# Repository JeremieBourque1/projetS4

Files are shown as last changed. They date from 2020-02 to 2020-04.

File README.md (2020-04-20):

# RoboAide



## Description
RoboAide is a project to improve a DIY robotic arm used for mobility assistance. This repository contains code for a GUI application, Arduino code for the control of the arm's motors as well as CAD parts for a 3D printed shell for the arm segments and joints. The application is made in Python using PySide2 and communicates the desired motor positions via USB serial communication with the Arduio/OpenCR board.<br/>
Due to the team's limitation in regards to access to the robotic arm, a smaller prototype version of the arm was built and it was with it that the software was written and tested on. However, the 3D printed shell was designed for the actual arm. In a future version, the software will be adapted for the real arm as well.

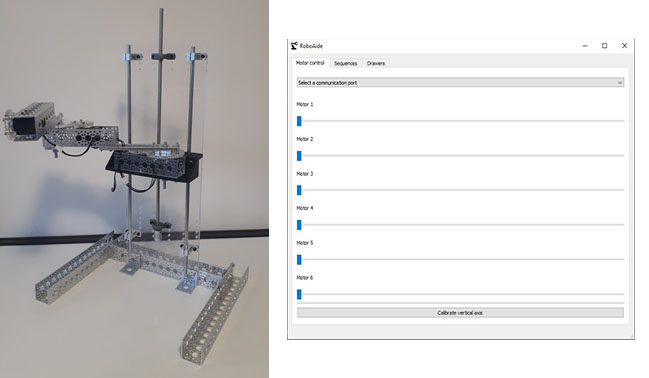
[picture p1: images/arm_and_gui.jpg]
Image of arm prototype and GUI app


## Overview of the application

The application is written in Python and is designed to run on Windows but should also run on other platforms, although this was not tested extensively.
The application contains three tabs: "Motor control", which is for moving the arm's motors individually in joint mode, "Sequences", which is for creating move sequences and executing them, and "Drawers", which is for opening and closing drawers.
It is to be noted that the code controlling the arm is split into two parts.The first is in the main and runs the openCR code for all of the arm's movements. The second is in the Vertical_Axis branch and runs the arduino code which moves the vertical motor.

*NOTE*: follow the instructions section before launching the application.

### Motor control
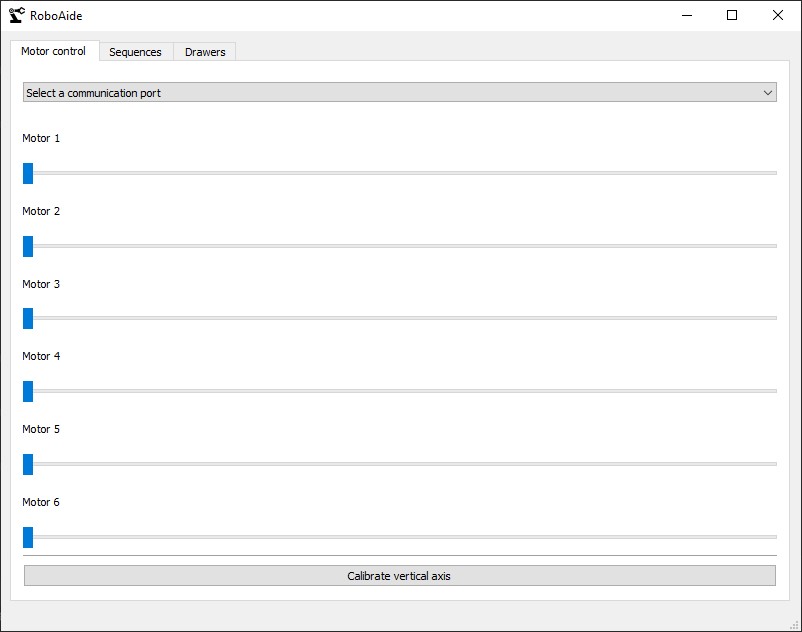
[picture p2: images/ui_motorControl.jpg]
Image of the motor control tab
<br/>
To start the connection, select the appropriate communication port in the drop-down menu. Once connected, moving the sliders will move the motors.

### Sequences
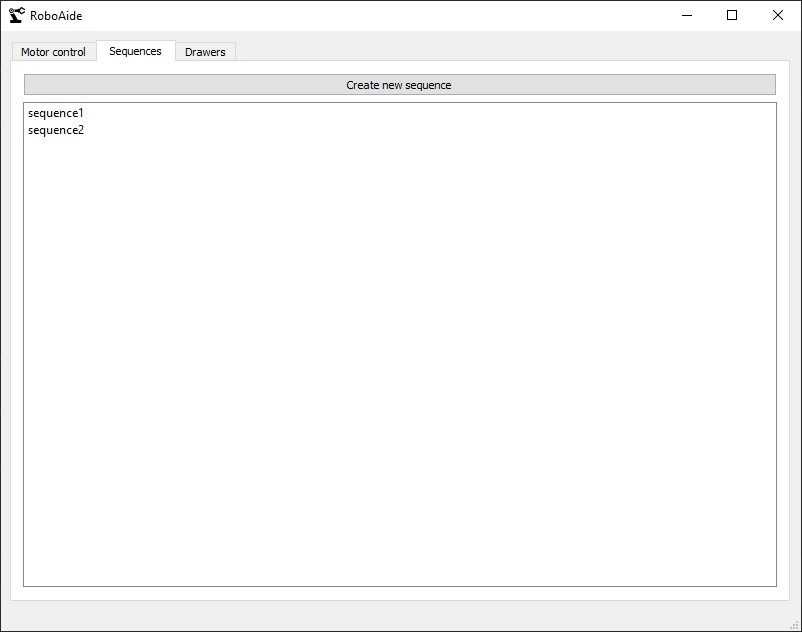
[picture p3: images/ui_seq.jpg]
Image of the sequences tab
<br/>
Here, you can see the list of user-created sequences. To execute a sequence, double click the sequence.<br/><br/>
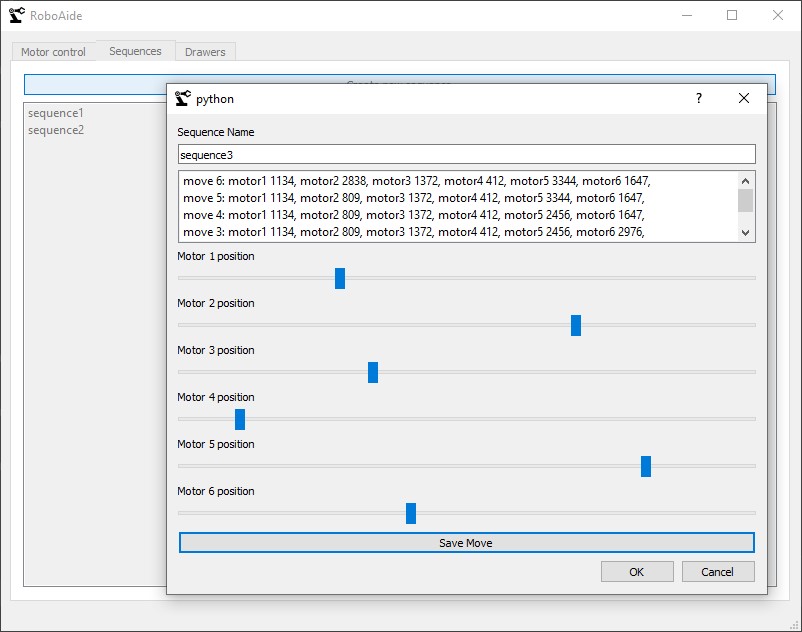
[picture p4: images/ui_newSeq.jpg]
Image of the new sequence window
<br/>
To create a new sequence, click the "Create new sequence" button, which will open this window. You can move the sliders to the desired position, then click "Save move" and create the next move. Double clicking a saved move will move the arm to that position. When done, click "ok".

### Drawers
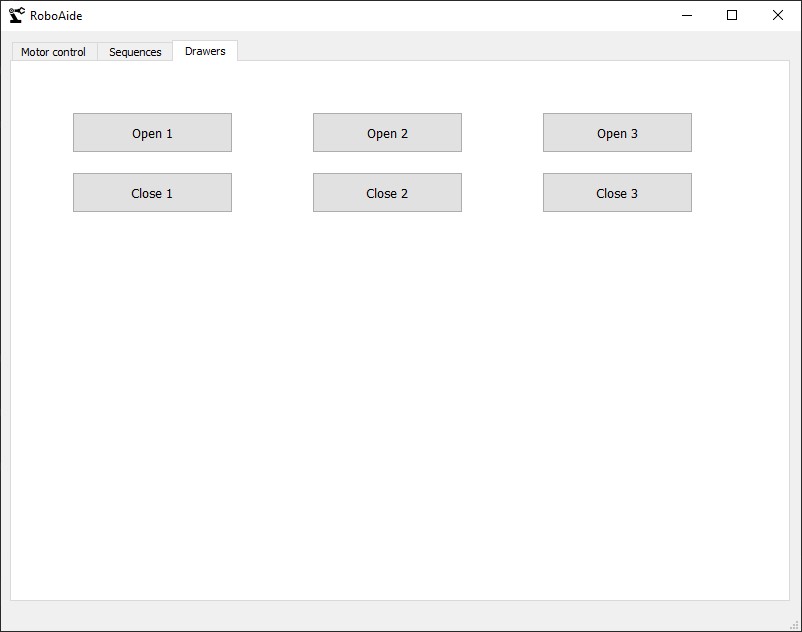
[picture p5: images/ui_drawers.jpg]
Image of the drawers tab
<br/>
This tab makes it possible to open and close the drawers. Note that this feature is not yet implemented in the controller, so the buttons currently do nothing. The feature will be implemented in a future version.

## Hardware Requirements
* 1x PC running Windows (may also run on other platforms, but hasn't been tested)
* 1x OpenCR board
* 3x Dynamixel motors
* 2x Twidec NJK-5002J inductive proximity sensor
* 1x L298N DC motor drive
* 1x Cytron 12v DC motor
* Robot arm prototype (see hardware documentation for more information)

## Software requirements

### UI Dependencies
* Python 3.7 or later (https://www.python.org/downloads/)
* pip (https://www.liquidweb.com/kb/install-pip-windows/)
* PySide2 
* PySerial

The necessary Python libraries can be installed with `pip install -r requirements.txt`

### Controller dependencies
* Arduino IDE (https://www.arduino.cc/en/main/software)
* OpenCR driver (should install automatically when the board is plugged into the PC)
* OpenCR board support for Arduino IDE (http://emanual.robotis.com/docs/en/parts/controller/opencr10/#install-on-windows)

## Instructions for the robot arm
1. Install all dependencies
2. Plug in the OpenCR board to the PC via USB
3. Launch Arduino IDE and choose the right board and communication port.
4. Upload the Arduino code
5. Run RoboAide.py with python to launch the GUI application. To do this, open a command prompt, change the directory to this project's directory and run this command `python UI/RoboAide.py`

## Instruction for the vertical axis
1. Plug all electronic according to the wiring diagram (see below)
2. Once plugged in, run and push the main.ino code which is under the Arduino_code folder to your arduino.
3. Open Pycharm and run the RoboAide.py file which can be found under the ui folder.
4. An application should pop up. Choose your communication port on the application and wait for 10 seconds to let the arduino initialise its comm port.
5. The vertical axis is ready to be calibrated. Press "calibrate vertical axis" button. Once the robot arm has been calibrated, you're free to use the 
slider #4 to move the vertical axis.

## Software documentation
All software documentation can be viewed [here](https://jeremiebourque1.github.io/projetS4/)

## Hardware documentation
### Robotic arm prototype
*The bill of materials for the robot arm prototype can be viewed [here](https://github.com/JeremieBourque1/projetS4/blob/master/BOM_proto.xlsx?raw=true)
* OpenCR documentation can be viewed [here](https://github.com/JeremieBourque1/projetS4/blob/master/electronic/OpenCR/robotis-opencr10-cortex-microcontroller-ros-datasheet.pdf)
* Electrical diagram of the prototype

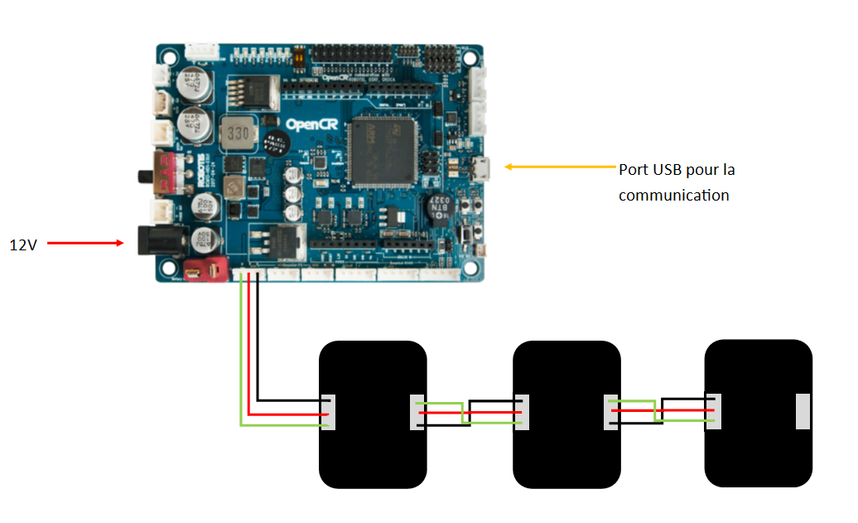
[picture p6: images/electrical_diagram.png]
Image of the electrical diagram

### Robotic arm shell
Everything concerning the arm shell can be found [here](https://github.com/JeremieBourque1/projetS4/tree/master/Arm%20Shell)
### Vertical axis
* DC driver L298N documentation can be viewed [here](https://github.com/JeremieBourque1/projetS4/blob/master/electronic/DC%20motor%20drive/L298N%20Motor%20Driver.pdf)
* Twidec NJK-5002J Inductive limit switch documentation can be viewed [here](https://github.com/JeremieBourque1/projetS4/blob/master/electronic/Limit%20switch/Twidec%20NJK-5002C%20SpecSheet.pdf)
* Cytron 12v DC motor documentation can be viewed [here](https://github.com/JeremieBourque1/projetS4/tree/master/electronic/Cytron%20DC%20motor)
* For wiring images using arduino mega2560 : 

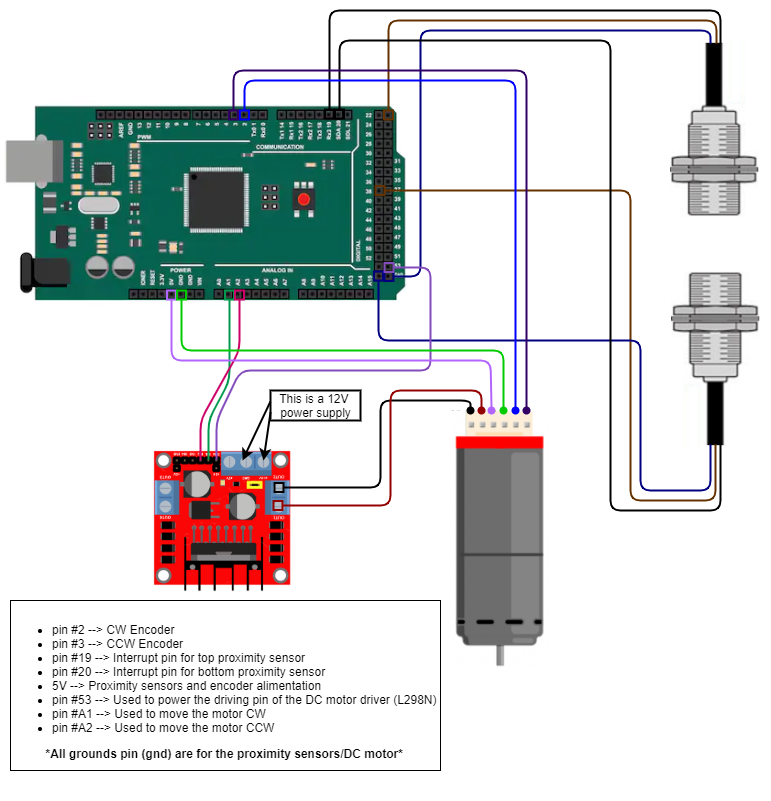
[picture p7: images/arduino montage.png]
Image of the wiring


## Unit tests
The application is tested using the unittest python module. To run the tests, open a command prompt, change the directory to the project’s directory and run this command: `python -m unittest discover`

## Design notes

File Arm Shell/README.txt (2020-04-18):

## Arm Shell

## Description

The arm is divided in two parts. The first part of the arm is the first joint starting from the wall and the second is starting at the elbow joint to the tool.
For each part there is a different shell and each shell will be printed in two pieces that will need to be assembled to the arm. 

## Assembling

For the first shell, each piece of the shell have 3 holes on small beams. In those holes, you must weld an insert (you can find what insert to use in the shell's BOM).
You will then be able to screw the tho parts together around the first joint (BOM for the screws to use). That will protect the cables and avoid fabric to get stuck in the gears.
You will do the same thing for the second shell.

** Use the Solidworks assembly to see how the shells should fit on the arm and where they go on the arm. **

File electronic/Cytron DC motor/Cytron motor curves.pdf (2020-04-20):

## RB-Cyt-90

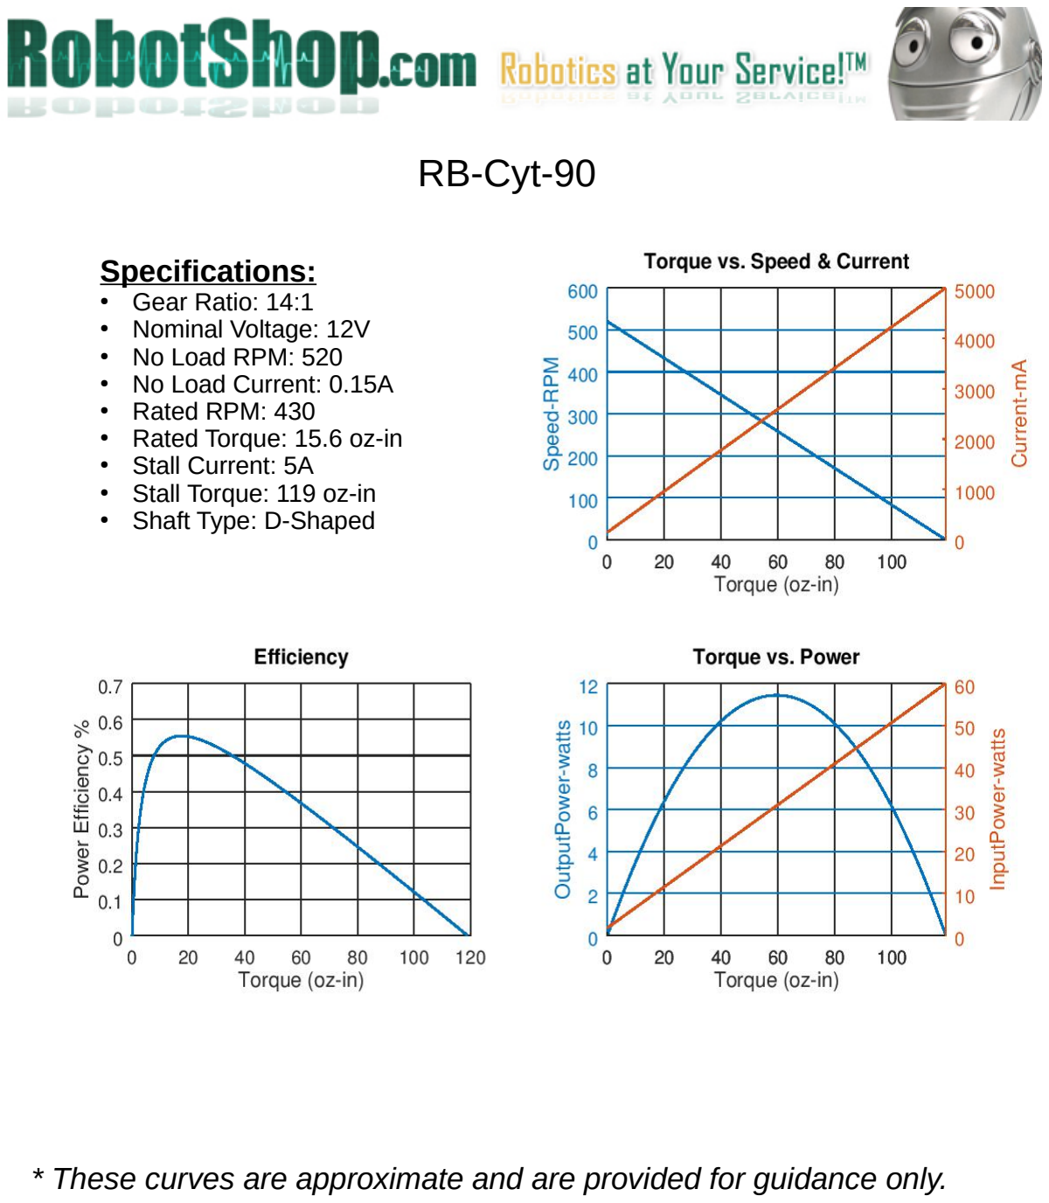
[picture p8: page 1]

* These curves are approximate and are provided for guidance only.

### Specifications:

- Gear Ratio: 14:1
- Nominal Voltage: 12V
- No Load RPM: 520
- No Load Current: 0.15A
- Rated RPM: 430
- Rated Torque: 15.6 oz-in
- Stall Current: 5A
- Stall Torque: 119 oz-in
- Shaft Type: D-Shaped

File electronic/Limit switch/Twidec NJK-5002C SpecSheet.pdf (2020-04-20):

# Inductive proximity switch NPN

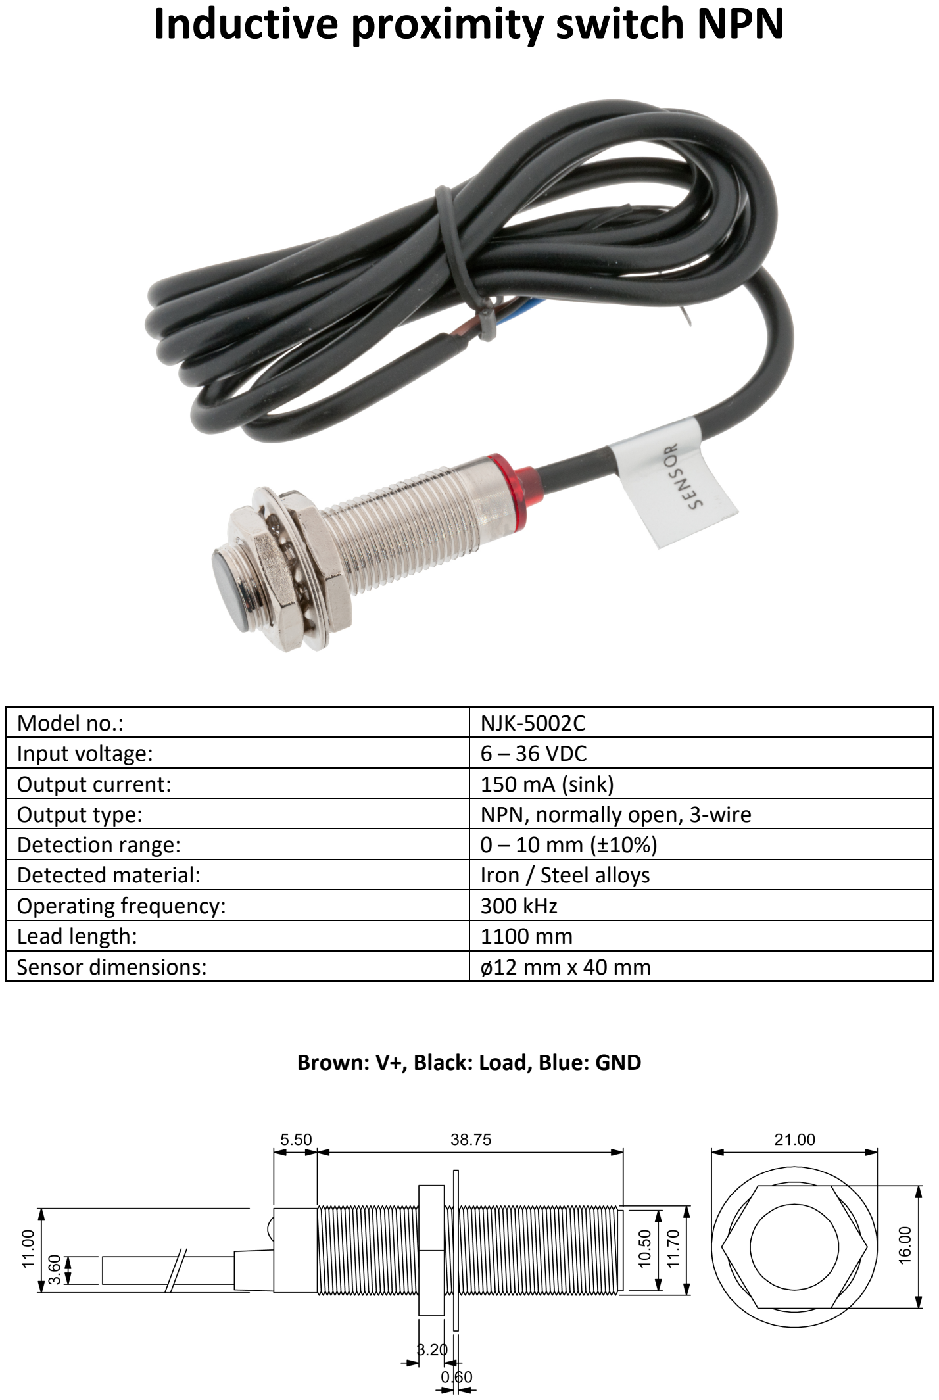
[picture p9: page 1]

Brown: V+, Black: Load, Blue: GND

Model no.: | NJK-5002C
Input voltage: | 6 – 36 VDC
Output current: | 150 mA (sink)
Output type: | NPN, normally open, 3-wire
Detection range: | 0 – 10 mm (±10%)
Detected material: | Iron / Steel alloys
Operating frequency: | 300 kHz
Lead length: | 1100 mm
Sensor dimensions: | ø12 mm x 40 mm

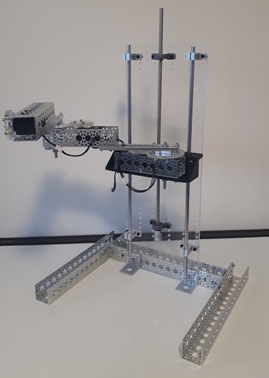
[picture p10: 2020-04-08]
images/arm_prototype.png

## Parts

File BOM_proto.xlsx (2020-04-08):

Bill of material for the prototype
Assembly part number | Description | Quantity | Vendor | Vendor part number | Link to vendor's website
1 | Motor | 3 | Dynamixel | XM-H-430 | http://www.robotis.us/search.php?search_query=xm%20h%20430&section=product
2 | vertical axel kit | 1 | Amazon - BQLZR | none | https://www.amazon.ca/gp/product/B01K4MVXOU/ref=ppx_yo_dt_b_asin_title_o00_s00?ie=UTF8&psc=1
3 | DC Planetary Gearmotor | 1 | RobotShop | Cytron 12V, 430rpm, 15.57oz-in Gear Motor w / Encoder | https://www.robotshop.com/en/cytron-12v-430rpm-15-57oz-gear-motor-encoder.html
4 | 1/4" x 4'' Stainless Steel D-Shafting | 2 | Servocity | 634080 | https://www.servocity.com/0-250-1-4-stainless-steel-d-shafting
5 | 12” Aluminum Channel | 3 | Servocity | 585454 | https://www.servocity.com/12-0-channel
6 | 1/4” Quad Pillow Block | 4 | Servocity | 535130 | https://www.servocity.com/250-bore-quad-pillow-block
7 | 6'' alluminium channel | 3 | Servocity | 585446 | https://www.servocity.com/6-0-channel
8 | 6.16” Aluminum Beam | 2 x 2 | Servocity | 585416 | https://www.servocity.com/6-16-aluminum-beam
9 | 90 Degree Single Angle Channel Bracket | 6 | Servocity | 585424 | https://www.servocity.com/90-single-angle-channel-bracket
10 | Flat Single Channel Bracket | 4 | Servocity | 585468 | https://www.servocity.com/flat-single-channel-bracket
11 | Bracket | 1 | PLA 3D printed | Proto_bracket_vertical | see 3D CAD
12 | Motor head bracket | 2 | acryliq laser cut | Support_engrenage_proto | see 3D CAD
13 | Custom gear 1 | 2 | acryliq laser cut | Parametric_pinion_V1.1, config Proto 1 | see 3D CAD
14 | Custom gear 2 | 2 | acryliq laser cut | Parametric_pinion_V1.1, config Proto 2 | see 3D CAD
15 | Vertical support plate | 1 | acryliq laser cut | Proto_base_verticale | see 3D CAD
16 | Horizontal support plate | 1 | wood laser cut | Base_proto | see 3D CAD
17 | Motor bracket | 1 | PLA 3D printed | none | see 3D CAD
18 | Screw M3 x 30 mm | 16 | Hardware store | none | Visit a hardware store
19 | Nut M3 | 16 | Hardware store | none | Visit a hardware store
20 | Screw #5-40, 3/4'' length | 16 | Hardware store | none | Visit a hardware store
21 | Screw #5-40, 1/2'' length | 16 | Hardware store | none | Visit a hardware store
22 | Screw #5-40, 3/8'' length | 28 | Hardware store | none | Visit a hardware store
23 | Nut #5-40 | 60 | Hardware store | none | Visit a hardware store
24 | Motor shaft adaptator | 1 | PLA 3D printed | none | see 3D CAD

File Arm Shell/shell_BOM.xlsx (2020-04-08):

https://www.mcmaster.com/screws
 |  |  | hauteur insert | 0,186 po
 | Bill of material for shell
 | Desciption | Vendor | Part number | Quantity | Link
 | Brass Heat-Set Insert for Plastic | McMaster | 94459A290 | 8 | https://www.mcmaster.com/94459a290
 | 18-8 Stainless Steel Socket Head Screw 2 3/4" | McMaster | 92196A263 (https://www.mcmaster.com/92196A263) | 6 | https://www.mcmaster.com/92196a263
 | 18-8 Stainless Steel Socket Head Screw 1" | McMaster | 92196A153 | 8 | https://www.mcmaster.com/92196a153
 | Dremel 3D Filament - PLA Orange | Home Dépot | 1000819406 | 1 | https://www.homedepot.ca/produit/dremel-3d-filament-pla-orange/1000819406?searchterm=1000819406

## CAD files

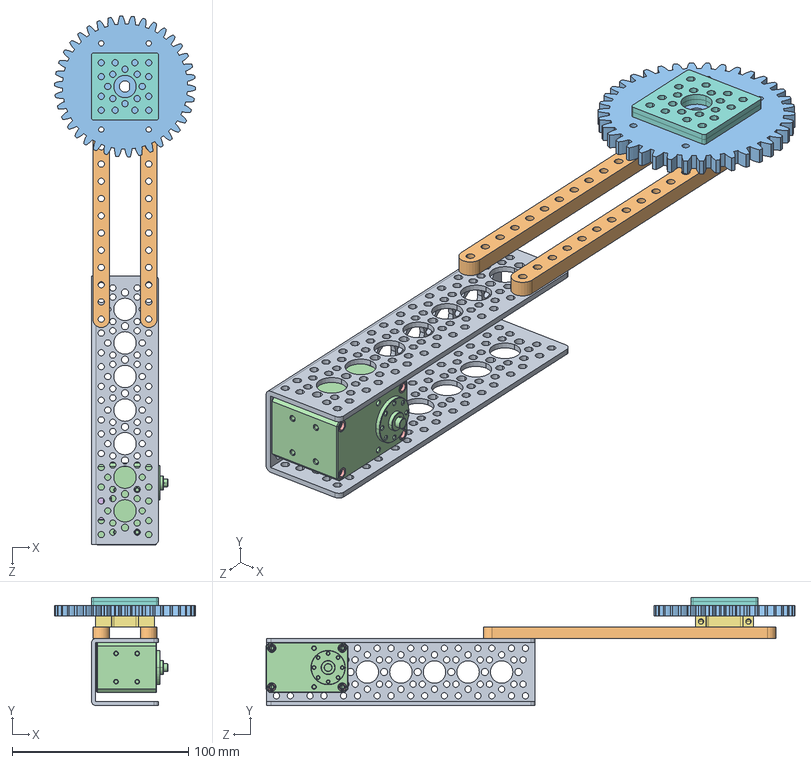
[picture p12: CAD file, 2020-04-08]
CAD_prototype/Proto_seg3_ASSY.SLDASM
80.0 x 61.4 x 300.1 mm
Parametric_pinion_V1.1
X-430_IDLE.stp
X-430_SPACER_RING.stp x 8
X-430_CVR_CABLE.stp
535130 assembly

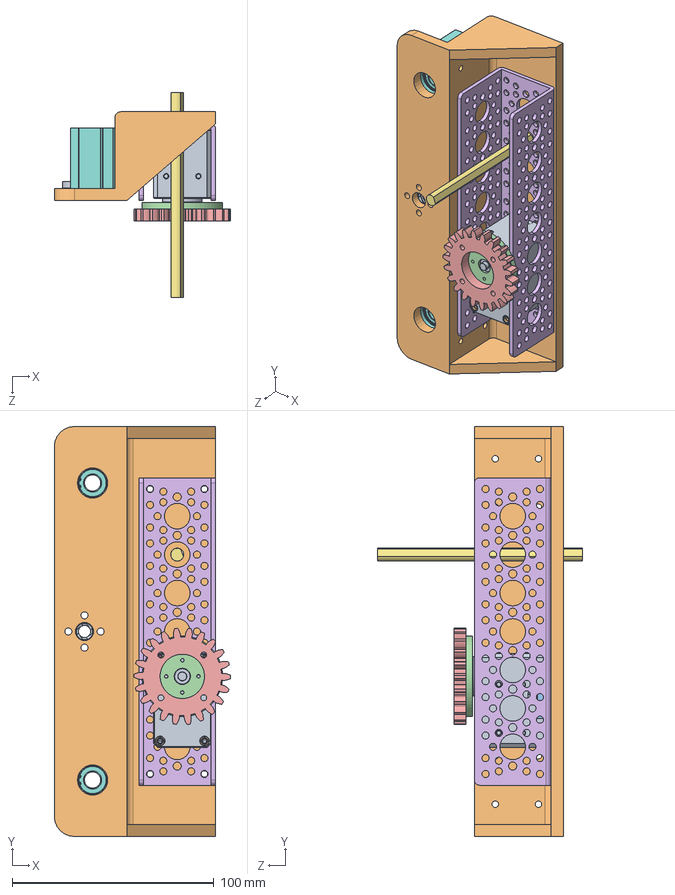
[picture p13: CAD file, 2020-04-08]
CAD_prototype/Proto_seg1_ASSY.SLDASM
87.5 x 203.2 x 101.6 mm
X-430_IDLE.stp
X-430_SPACER_RING.stp x 8
X-430_CVR_CABLE.stp
support_engrenage_proto
Parametric_pinion_V1.1
shaft_4po
SC8UU 8x34mm Slide Bushing x 2
Trapezoidal lead screw Nut tr8x8-4
proto_bracket_vertical

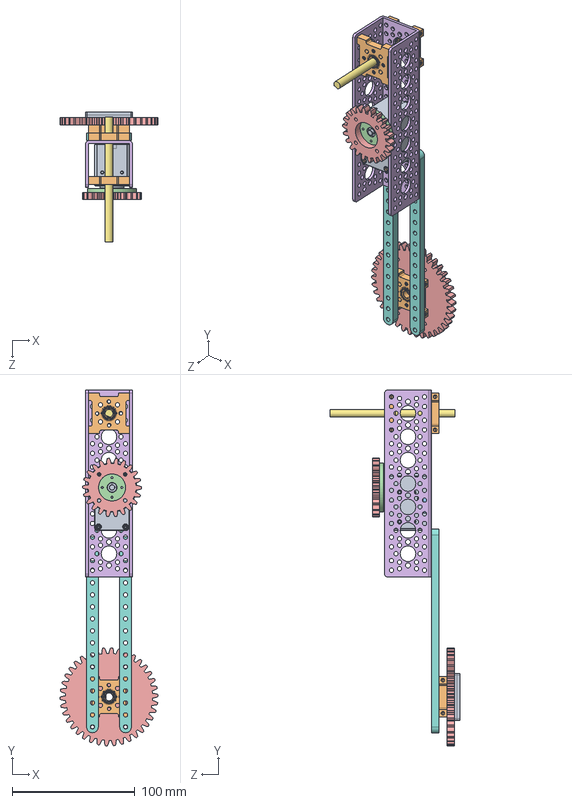
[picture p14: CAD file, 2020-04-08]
CAD_prototype/Proto_seg2_ASSY.SLDASM
80.0 x 290.0 x 105.8 mm
X-430_IDLE.stp
X-430_SPACER_RING.stp x 8
X-430_CVR_CABLE.stp
support_engrenage_proto
Parametric_pinion_V1.1 x 2
shaft_4po
535130 assembly x 3

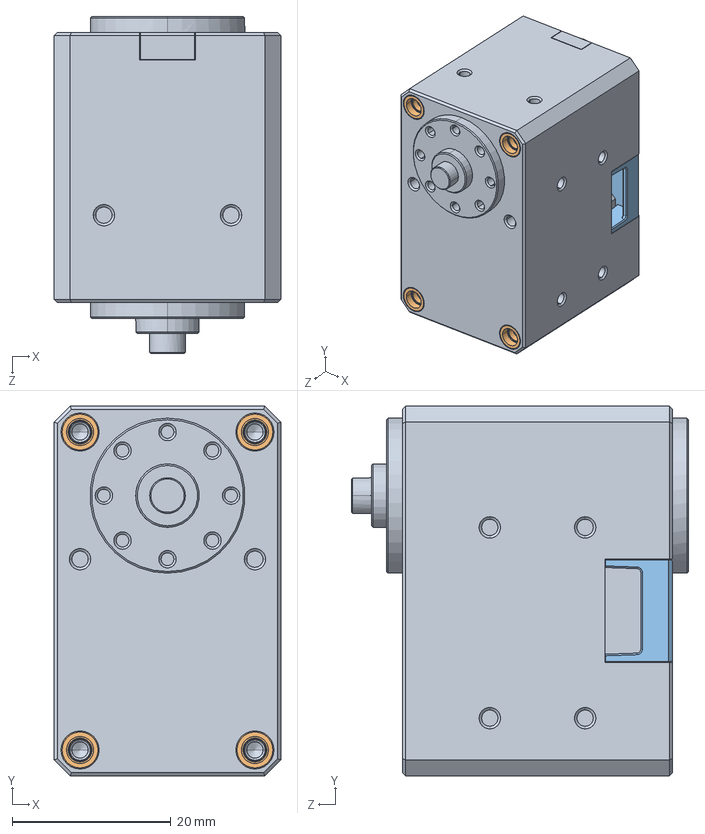
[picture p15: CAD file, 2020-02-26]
CAD_prototype/XM,H-430_idler.SLDASM
28.5 x 46.5 x 42.4 mm
X-430_IDLE.stp
X-430_SPACER_RING.stp x 8
X-430_CVR_CABLE.stp

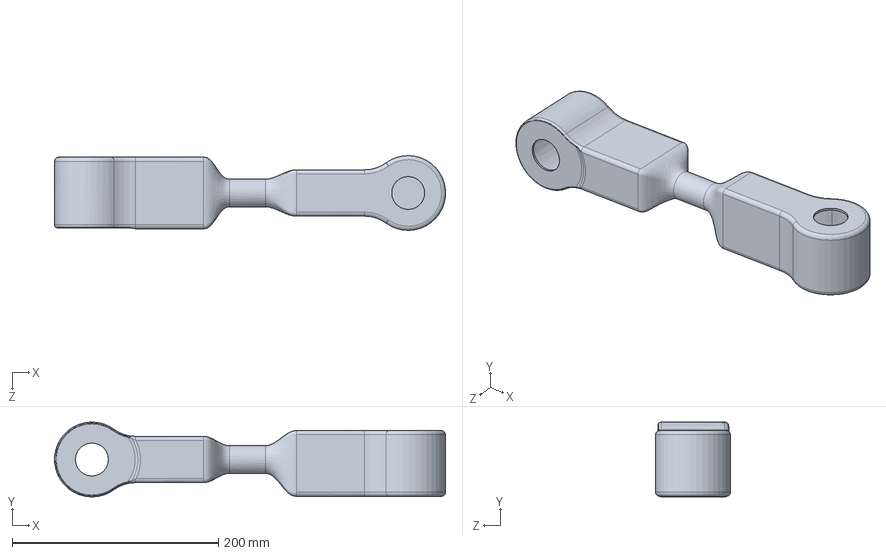
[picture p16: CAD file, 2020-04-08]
Arm Shell/SolidParts/second.SLDPRT
379.5 x 72.6 x 72.6 mm

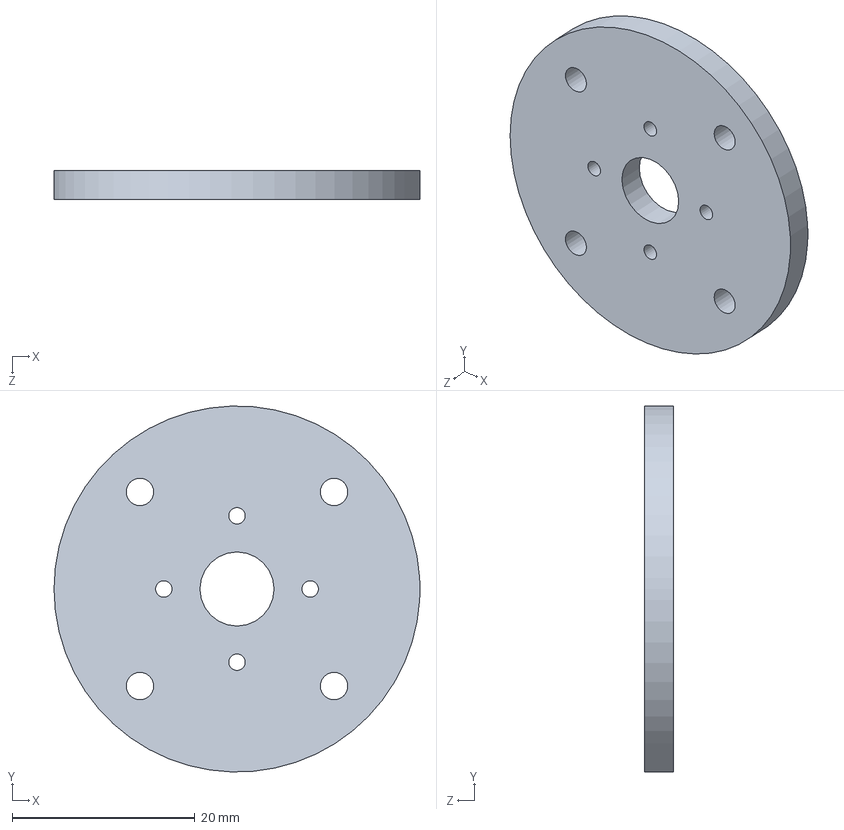
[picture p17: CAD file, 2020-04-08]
CAD_prototype/support_engrenage_proto.SLDPRT
40.0 x 40.0 x 3.17 mm

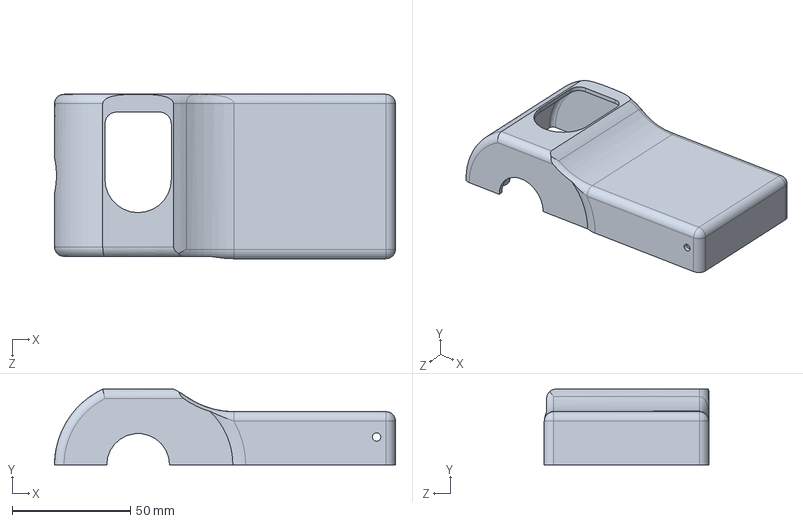
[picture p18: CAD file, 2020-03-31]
Arm Shell/SolidParts/coin_baseV2_troue.SLDPRT
144.0 x 32.0 x 69.5 mm

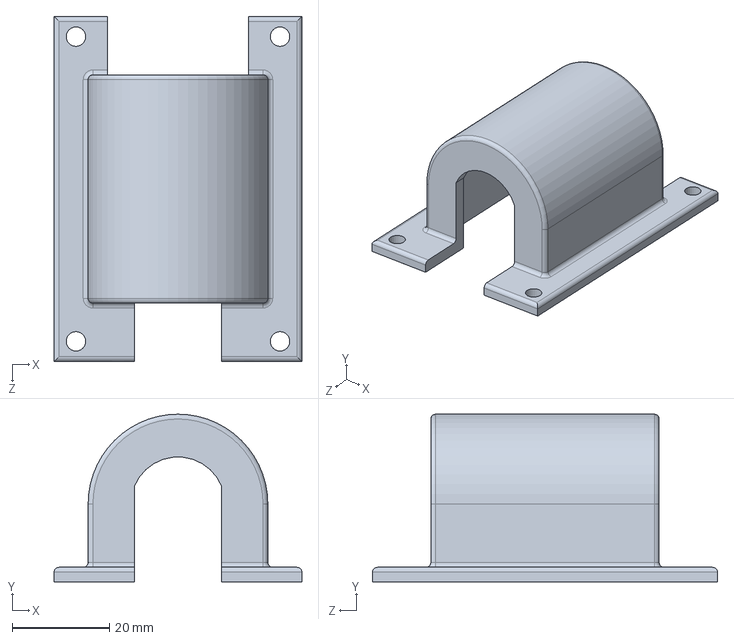
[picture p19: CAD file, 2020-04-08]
CAD_prototype/proto_motor_bracket.SLDPRT
51.0 x 34.5 x 71.0 mm

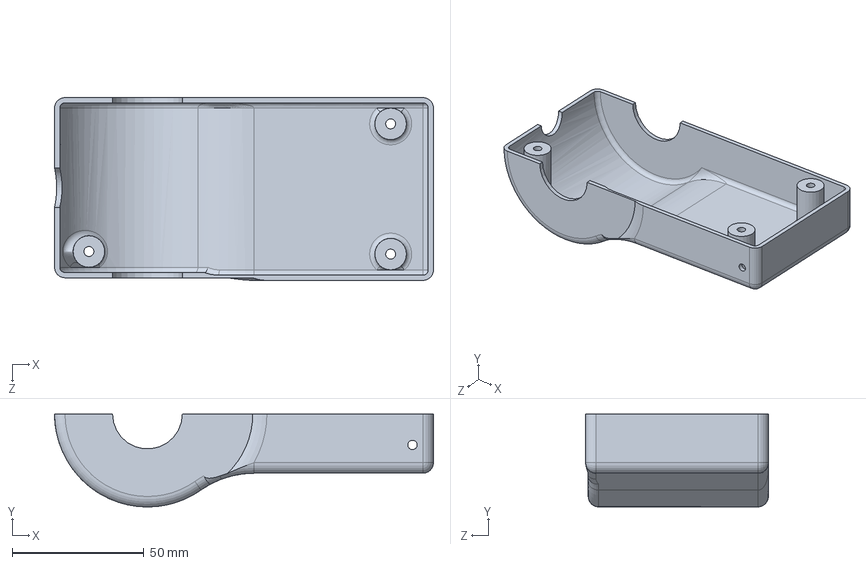
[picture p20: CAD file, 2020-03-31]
Arm Shell/SolidParts/coin_baseV2_top.SLDPRT
144.0 x 35.3 x 69.5 mm

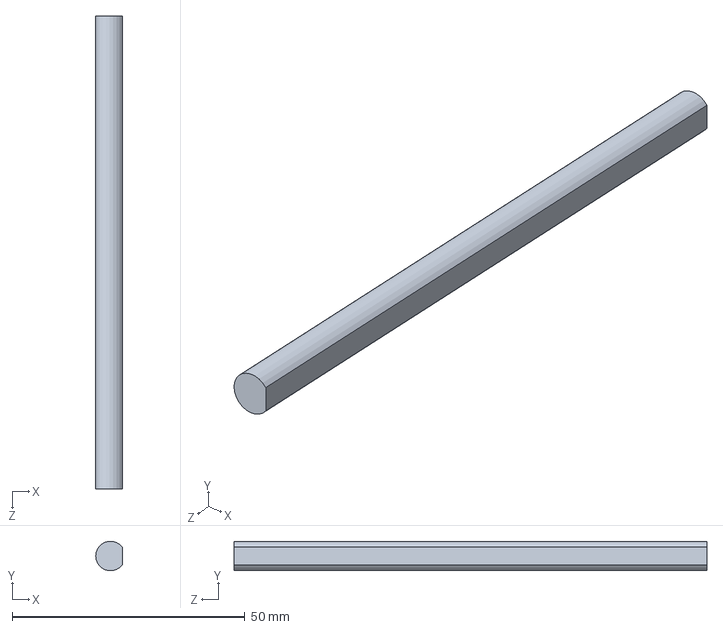
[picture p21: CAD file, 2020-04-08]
CAD_prototype/shaft_4po.SLDPRT
5.72 x 6.33 x 101.6 mm

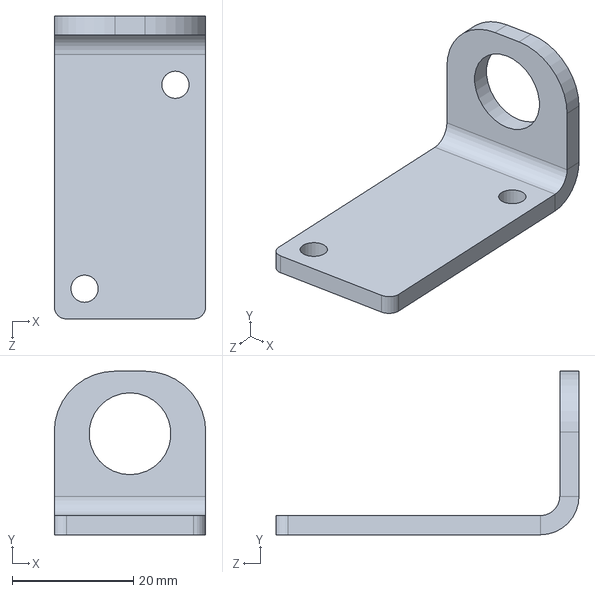
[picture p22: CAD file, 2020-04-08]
CAD_prototype/NJK-5002 Base Bracket.SLDPRT
25.0 x 27.0 x 50.0 mm

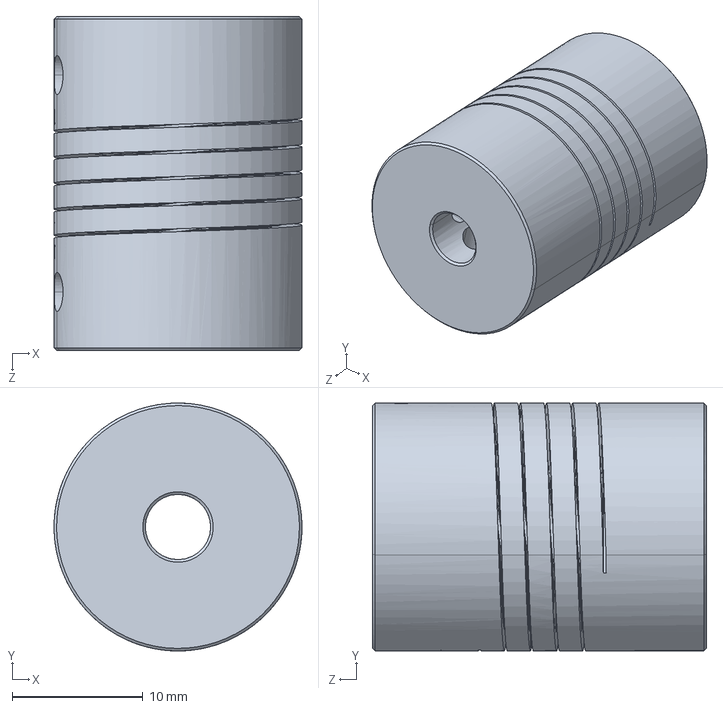
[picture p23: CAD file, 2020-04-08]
CAD_prototype/jaw shaft coupler 5x8mm.SLDPRT
19.0 x 19.0 x 25.6 mm

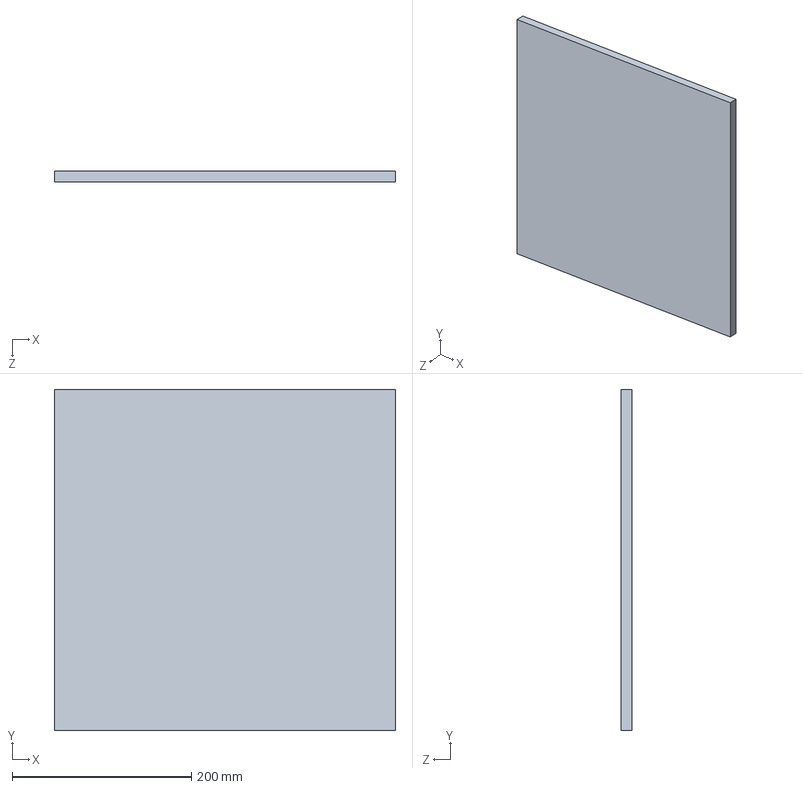
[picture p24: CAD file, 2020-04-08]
CAD_prototype/base_proto.SLDPRT
381.0 x 381.0 x 12.7 mm

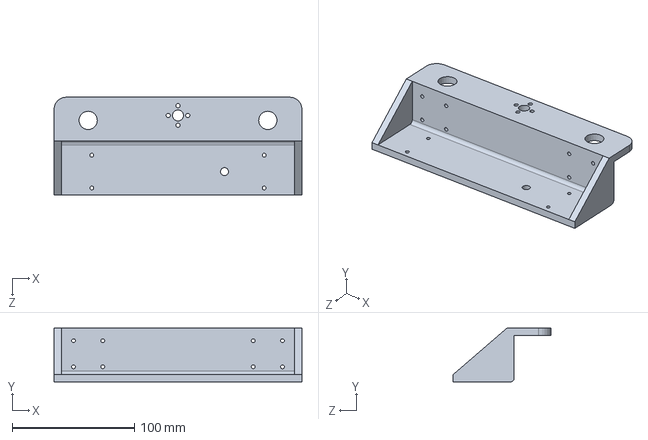
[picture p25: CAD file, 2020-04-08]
CAD_prototype/proto_bracket_vertical.SLDPRT
203.2 x 44.0 x 80.0 mm

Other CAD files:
CAD_prototype/KP08 bearing bracket.SLDPRT
CAD_prototype/proto_base_verticale.SLDPRT
CAD_prototype/adaptateur.SLDPRT
CAD_prototype/Cytron 430RPM.SLDPRT
CAD_prototype/535130 assembly.SLDPRT
CAD_prototype/585416.SLDPRT
CAD_prototype/585424.SLDPRT
CAD_prototype/585446.SLDPRT
CAD_prototype/585454.SLDPRT
CAD_prototype/585468.SLDPRT
CAD_prototype/Leadscrew.SLDPRT
CAD_prototype/Linear Rail Shaft Guide-Support - 8mm Diameter - SK8.SLDPRT
CAD_prototype/SC8UU 8x34mm Slide Bushing.SLDPRT
CAD_prototype/Trapezoidal lead screw Nut tr8x8-4.SLDPRT
CAD_prototype/proto_bracket_bearing.SLDPRT
CAD_prototype/spur gear_ai_proto.sldprt

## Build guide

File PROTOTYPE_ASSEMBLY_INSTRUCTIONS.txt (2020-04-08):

INSTRUCTIONS TO ASSEMBLE THE PROTOTYPE
****
In order to assemble the prototype, you must have the materials listed in the bill of materials.
Every part is assigned to its number from the BOM.
Use the CAD as additionnal information and guide to complete the assembly of the prototype.
****

1. Assemble the first segment of the arm with parts 1, 4, 6, 7, 2x 10, 11, 12, 13, 14, 4x 21, 4x 23, the lead screw from kit 2 and 2x linear bearing from kit 2.

2. Assemble the second segment of the arm with parts 1, 4, 3x 6, 7, 8, 2x 10, 12, 13, 14, 8x 21 and 8x 23.
 
3. Assemble the third segment of the arm with parts 1, 7, 8, 4x 21 and 4x 23.

4. Assemble segment 2 and 3 of the arm using 4x part 20 and 4x part 23.

5. Assemble segment 2/3 with the segment 1 using 4x part 20 and 4x part 23.

6. Insert the leading screw in the lead screw part and the guiding shaft in the linear bearing. Those parts are in the kit no.2.

7. Assemble the vertical support plate using the rest of the parts form kit 2 with parts 15, 3, 17, 16x 18 and 16x 19. 

8. Assemble the alluminium base support on the wood plank using parts 16, 3x 5, 4x 9, 24x 22 and 24x 23.

9. Assemble the robot arm to the base using 2x9, 4x 22 and 4x 23.

GOOD LUCK!

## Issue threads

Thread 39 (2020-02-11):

### ISSUE TITLE
CAD of all sub parts

### ISSUE THREAD

**Issue by Plopao** [JeremieBourque1/projetS4#39]
*LOOK IN THE CARS ABOUT CONVERTING FREE CAD TO SOLIDWORKS FIRST!*

- [x] Gears

- [ ] Axis holding the gears in place

- [ ] Arm segment (tubing)

- [x] Other brackets

**Comment by amelierioux** [comment]
We need to do more measurements of François's arm because we are missing some to complete all the parts.

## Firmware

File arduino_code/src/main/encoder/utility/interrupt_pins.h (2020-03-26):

// interrupt pins for known boards

// Teensy (and maybe others) define these automatically
#if !defined(CORE_NUM_INTERRUPT)

// Wiring boards
#if defined(WIRING)
  #define CORE_NUM_INTERRUPT	NUM_EXTERNAL_INTERRUPTS
  #if NUM_EXTERNAL_INTERRUPTS > 0
  #define CORE_INT0_PIN		EI0
  #endif
  #if NUM_EXTERNAL_INTERRUPTS > 1
  #define CORE_INT1_PIN		EI1
  #endif
  #if NUM_EXTERNAL_INTERRUPTS > 2
  #define CORE_INT2_PIN		EI2
  #endif
  #if NUM_EXTERNAL_INTERRUPTS > 3
  #define CORE_INT3_PIN		EI3
  #endif
  #if NUM_EXTERNAL_INTERRUPTS > 4
  #define CORE_INT4_PIN		EI4
  #endif
  #if NUM_EXTERNAL_INTERRUPTS > 5
  #define CORE_INT5_PIN		EI5
  #endif
  #if NUM_EXTERNAL_INTERRUPTS > 6
  #define CORE_INT6_PIN		EI6
  #endif
  #if NUM_EXTERNAL_INTERRUPTS > 7
  #define CORE_INT7_PIN		EI7
  #endif

// Arduino Uno, Duemilanove, Diecimila, LilyPad, Mini, Fio, etc...
#elif defined(__AVR_ATmega328P__) || defined(__AVR_ATmega328PB__) ||defined(__AVR_ATmega168__) || defined(__AVR_ATmega8__)
  #define CORE_NUM_INTERRUPT	2
  #define CORE_INT0_PIN		2
  #define CORE_INT1_PIN		3

// Arduino Mega
#elif defined(__AVR_ATmega1280__) || defined(__AVR_ATmega2560__)
  #define CORE_NUM_INTERRUPT	6
  #define CORE_INT0_PIN		2
  #define CORE_INT1_PIN		3
  #define CORE_INT2_PIN		21
  #define CORE_INT3_PIN		20
  #define CORE_INT4_PIN		19
  #define CORE_INT5_PIN		18

// Arduino Nano Every, Uno R2 Wifi
#elif defined(__AVR_ATmega4809__)
  #define CORE_NUM_INTERRUPT	13
  #define CORE_INT0_PIN		0
  #define CORE_INT1_PIN		1
  #define CORE_INT2_PIN		2
  #define CORE_INT3_PIN		3
  #define CORE_INT4_PIN		4
  #define CORE_INT5_PIN		5
  #define CORE_INT6_PIN		6
  #define CORE_INT7_PIN		7
  #define CORE_INT8_PIN		8
  #define CORE_INT9_PIN		9
  #define CORE_INT10_PIN	10
  #define CORE_INT11_PIN	11
  #define CORE_INT12_PIN	12
  #define CORE_INT13_PIN	13

// Arduino Leonardo (untested)
#elif defined(__AVR_ATmega32U4__) && !defined(CORE_TEENSY)
  #define CORE_NUM_INTERRUPT	5
  #define CORE_INT0_PIN		3
  #define CORE_INT1_PIN		2
  #define CORE_INT2_PIN		0
  #define CORE_INT3_PIN		1
  #define CORE_INT4_PIN		7

// Sanguino (untested) and ATmega1284P
#elif defined(__AVR_ATmega644P__) || defined(__AVR_ATmega644__) || defined(__AVR_ATmega1284P__)
  #define CORE_NUM_INTERRUPT	3
  #define CORE_INT0_PIN		10
  #define CORE_INT1_PIN		11
  #define CORE_INT2_PIN		2

// ATmega32u2 and ATmega32u16 based boards with HoodLoader2
#elif defined(__AVR_ATmega32U2__) || defined(__AVR_ATmega16U2__)
  #define CORE_NUM_INTERRUPT 8
  #define CORE_INT0_PIN 8
  #define CORE_INT1_PIN 17
  #define CORE_INT2_PIN 13
  #define CORE_INT3_PIN 14
  #define CORE_INT4_PIN 15
  #define CORE_INT5_PIN 16
  #define CORE_INT6_PIN 19
  #define CORE_INT7_PIN 20

// Chipkit Uno32 - attachInterrupt may not support CHANGE option
#elif defined(__PIC32MX__) && defined(_BOARD_UNO_)
  #define CORE_NUM_INTERRUPT	5
  #define CORE_INT0_PIN		38
  #define CORE_INT1_PIN		2
  #define CORE_INT2_PIN		7
  #define CORE_INT3_PIN		8
  #define CORE_INT4_PIN		35

// Chipkit Uno32 - attachInterrupt may not support CHANGE option
#elif defined(__PIC32MX__) && defined(_BOARD_MEGA_)
  #define CORE_NUM_INTERRUPT	5
  #define CORE_INT0_PIN		3
  #define CORE_INT1_PIN		2
  #define CORE_INT2_PIN		7
  #define CORE_INT3_PIN		21
  #define CORE_INT4_PIN		20

// http://hlt.media.mit.edu/?p=1229
#elif defined(__AVR_ATtiny45__) || defined(__AVR_ATtiny85__)
  #define CORE_NUM_INTERRUPT    1
  #define CORE_INT0_PIN		2

// ATtiny441 ATtiny841
#elif defined(__AVR_ATtiny441__) || defined(__AVR_ATtiny841__)
  #define CORE_NUM_INTERRUPT	1
  #define CORE_INT0_PIN		9

//https://github.com/SpenceKonde/ATTinyCore/blob/master/avr/extras/ATtiny_x313.md
#elif defined(__AVR_ATtinyX313__)
  #define CORE_NUM_INTERRUPT    2
  #define CORE_INT0_PIN		4
  #define CORE_INT1_PIN		5
 
// Attiny167 same core as abobe
#elif defined(__AVR_ATtiny167__)
  #define CORE_NUM_INTERRUPT	2
  #define CORE_INT0_PIN		14
  #define CORE_INT1_PIN		3

  
// Arduino Due
#elif defined(__SAM3X8E__) 
  #define CORE_NUM_INTERRUPT	54
  #define CORE_INT0_PIN		0
  #define CORE_INT1_PIN		1
  #define CORE_INT2_PIN		2
  #define CORE_INT3_PIN		3
  #define CORE_INT4_PIN		4
  #define CORE_INT5_PIN		5
  #define CORE_INT6_PIN		6
  #define CORE_INT7_PIN		7
  #define CORE_INT8_PIN		8
  #define CORE_INT9_PIN		9
  #define CORE_INT10_PIN	10
  #define CORE_INT11_PIN	11
  #define CORE_INT12_PIN	12
  #define CORE_INT13_PIN	13
  #define CORE_INT14_PIN	14
  #define CORE_INT15_PIN	15
  #define CORE_INT16_PIN	16
  #define CORE_INT17_PIN	17
  #define CORE_INT18_PIN	18
  #define CORE_INT19_PIN	19
  #define CORE_INT20_PIN	20
  #define CORE_INT21_PIN	21
  #define CORE_INT22_PIN	22
  #define CORE_INT23_PIN	23
  #define CORE_INT24_PIN	24
  #define CORE_INT25_PIN	25
  #define CORE_INT26_PIN	26
  #define CORE_INT27_PIN	27
  #define CORE_INT28_PIN	28
  #define CORE_INT29_PIN	29
  #define CORE_INT30_PIN	30
  #define CORE_INT31_PIN	31
  #define CORE_INT32_PIN	32
  #define CORE_INT33_PIN	33
  #define CORE_INT34_PIN	34
  #define CORE_INT35_PIN	35
  #define CORE_INT36_PIN	36
  #define CORE_INT37_PIN	37
  #define CORE_INT38_PIN	38
  #define CORE_INT39_PIN	39
  #define CORE_INT40_PIN	40
  #define CORE_INT41_PIN	41
  #define CORE_INT42_PIN	42
  #define CORE_INT43_PIN	43
  #define CORE_INT44_PIN	44
  #define CORE_INT45_PIN	45
  #define CORE_INT46_PIN	46
  #define CORE_INT47_PIN	47
  #define CORE_INT48_PIN	48
  #define CORE_INT49_PIN	49
  #define CORE_INT50_PIN	50
  #define CORE_INT51_PIN	51
  #define CORE_INT52_PIN	52
  #define CORE_INT53_PIN	53

// ESP8266 (https://github.com/esp8266/Arduino/)
#elif defined(ESP8266)
  #define CORE_NUM_INTERRUPT EXTERNAL_NUM_INTERRUPTS
  #define CORE_INT0_PIN		0
  #define CORE_INT1_PIN		1
  #define CORE_INT2_PIN		2
  #define CORE_INT3_PIN		3
  #define CORE_INT4_PIN		4
  #define CORE_INT5_PIN		5
  // GPIO6-GPIO11 are typically used to interface with the flash memory IC on 
  // most esp8266 modules, so we should avoid adding interrupts to these pins.
  #define CORE_INT12_PIN	12
  #define CORE_INT13_PIN	13
  #define CORE_INT14_PIN	14
  #define CORE_INT15_PIN	15

// ESP32 (https://github.com/espressif/arduino-esp32)
#elif defined(ESP32)

  #define CORE_NUM_INTERRUPT  40 
  #define CORE_INT0_PIN		0
  #define CORE_INT1_PIN		1
  #define CORE_INT2_PIN		2
  #define CORE_INT3_PIN		3
  #define CORE_INT4_PIN		4
  #define CORE_INT5_PIN		5
  // GPIO6-GPIO11 are typically used to interface with the flash memory IC on 
  // esp32, so we should avoid adding interrupts to these pins.
  #define CORE_INT12_PIN	12
  #define CORE_INT13_PIN	13
  #define CORE_INT14_PIN	14
  #define CORE_INT15_PIN	15
  #define CORE_INT16_PIN        16
  #define CORE_INT17_PIN        17
  #define CORE_INT18_PIN        18
  #define CORE_INT19_PIN        19
  #define CORE_INT21_PIN        21
  #define CORE_INT22_PIN        22
  #define CORE_INT23_PIN        23
  #define CORE_INT25_PIN        25
  #define CORE_INT26_PIN        26
  #define CORE_INT27_PIN        27
  #define CORE_INT32_PIN        32
  #define CORE_INT33_PIN        33
  #define CORE_INT34_PIN        34
  #define CORE_INT35_PIN        35
  #define CORE_INT36_PIN        36
  #define CORE_INT39_PIN        39


// Arduino Zero - TODO: interrupts do not seem to work
//                      please help, contribute a fix!
#elif defined(__SAMD21G18A__) || defined(__SAMD51__)
  #define CORE_NUM_INTERRUPT	20
  #define CORE_INT0_PIN		0
  #define CORE_INT1_PIN		1
  #define CORE_INT2_PIN		2
  #define CORE_INT3_PIN		3
  #define CORE_INT5_PIN		5
  #define CORE_INT6_PIN		6
  #define CORE_INT7_PIN		7
  #define CORE_INT8_PIN		8
  #define CORE_INT9_PIN		9
  #define CORE_INT10_PIN	10
  #define CORE_INT11_PIN	11
  #define CORE_INT12_PIN	12
  #define CORE_INT13_PIN	13
  #define CORE_INT14_PIN	14
  #define CORE_INT15_PIN	15
  #define CORE_INT16_PIN	16
  #define CORE_INT17_PIN	17
  #define CORE_INT18_PIN	18
  #define CORE_INT19_PIN	19

// Arduino 101
#elif defined(__arc__)
  #define CORE_NUM_INTERRUPT	14
  #define CORE_INT2_PIN		2
  #define CORE_INT5_PIN		5
  #define CORE_INT7_PIN		7
  #define CORE_INT8_PIN		8
  #define CORE_INT10_PIN	10
  #define CORE_INT11_PIN	11
  #define CORE_INT12_PIN	12
  #define CORE_INT13_PIN	13

//OpenCR
#elif defined(__OPENCR__) || defined(__OPENCM904__)
  #define CORE_NUM_INTERRUPT	9
  #define CORE_INT0_PIN		0
  #define CORE_INT1_PIN		1
  #define CORE_INT2_PIN		2
  #define CORE_INT3_PIN		3
  #define CORE_INT4_PIN		4
  #define CORE_INT5_PIN		5
  #define CORE_INT6_PIN		6
  #define CORE_INT7_PIN		7
  #define CORE_INT8_PIN		8

#endif
#endif

#if !defined(CORE_NUM_INTERRUPT)
#error "Interrupts are unknown for this board, please add to this code"
#endif
#if CORE_NUM_INTERRUPT <= 0
#error "Encoder requires interrupt pins, but this board does not have any :("
#error "You could try defining ENCODER_DO_NOT_USE_INTERRUPTS as a kludge."
#endif

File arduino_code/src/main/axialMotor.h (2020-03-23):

class axialMotor
{
  public:
  axialMotor(int enAPin, int motorInitialState,int pinCWOutputValue, int pinCCWOutputValue, int ProxSensor1Value,int ProxSensor2Value);
  axialMotor();
  bool shouldSlowDown();
  bool runAxialCalibration();
  void setMotorState(int stateValue);
  void setEnableDrive(bool driveValue);
  int getMotorState();
  int getDriveState();
  int getProximitySensorPin(bool sensorNumber);
  int getProximitySensorValue(bool sensorNumber);
  int getMotorPin(int directionNumber);
  int getDrivePin();
  
  private:
  int motorState;
  int enAPin; //digital pin for enabling the motor control
  int pinCWOutput; //Pin for CW control (#1)
  int pinCCWOutput; //Pin for CCW control (#2)
  int proximitySensor1Pin; //Connected pin for sensor #1
  int proximitySensor2Pin; //Connected pin for sensor #2s
};

/** \brief Construct the axial motor with initial states/pinout
  * \param motorInitialState : Motor start state (0,1,-1). 0 means going CCW, 1 CW and -1 STOP.
  * \param ProxSensor1Value : Pin value of the first proximity sensor
  * \param ProxSensor2Value : Pin value of the second proximity sensor
  */
axialMotor::axialMotor(int enAPinValue, int motorInitialState,int pinCWOutputValue, int pinCCWOutputValue, int ProxSensor1Value,int ProxSensor2Value)
{
  motorState = motorInitialState;
  //setMotorState(motorState);
  enAPin = enAPinValue;
  pinCWOutput = pinCWOutputValue;
  pinCCWOutput = pinCCWOutputValue;  
  proximitySensor1Pin = ProxSensor1Value;
  proximitySensor2Pin = ProxSensor2Value;

}

/** \brief Construct the axial motor with no initial states/pinout. Motor state is then set to STOP (-1), and proximity sensor pinout to 51 and 53 by default.
  */
axialMotor::axialMotor()
{
  motorState = -1;
  //setMotorState(motorState);
  enAPin = 45;
  pinCWOutput = 47;
  pinCCWOutput = 49;  
  proximitySensor1Pin = 51;
  proximitySensor2Pin = 53;
}

/** \brief Checks if the requirement to make the motor stop are met. 
 *  /return bool : value confirming if the motor should slow down or not.
 */
bool axialMotor::shouldSlowDown()
{
 int proximitySensor1Reading = digitalRead(getProximitySensorPin(1)); //defines the input to pins #51. The input is HIGH when nothing is capted this is the top sensor
  //Serial.print("la valeur de proximite est de :");
  //Serial.print(proximitySensor1Reading);
  if (proximitySensor1Reading == false && getMotorState() == true || getMotorState() == -1)
  {
   // Serial.print("Je lis le capteur et le moteur monte");
    return true;
  }

  else if (proximitySensor1Reading == false && getMotorState() == false)
  {
    //Serial.print("Je lis le capteur et le moteur DESCEND");
    return false;
  }
  else
  {
    return false;
  }
 int proximitySensor2Reading = digitalRead(getProximitySensorPin(2)); //defines the input to pin #53. The input is HIGH when nothing is capted
 //Serial.print("TU ENTRE EN CAPTEUR 2!");

  if (proximitySensor2Reading == false && getMotorState() == true)
  {
  //  Serial.print("CAPTEUR 2 UNDER CONSTRUCTION");
    return false;
  }

  else if (proximitySensor2Reading == false && getMotorState() == false || getMotorState() == -1)
  {
   // Serial.print("CAPTEUR 2 UNDER CONSTRUCTION");
    return true;
  }
  
  else
  {
    return false;
  }
}

/** \brief Calibrate the assembly's vertical axis using the upper proximity sensor.
  * \param motorInitialState : Motor start state (0,1,-1). 0 means going CCW, 1 CW and -1 STOP.
  * \param ProxSensor1Value : Pin value of the first proximity sensor.
  * \param ProxSensor2Value : Pin value of the second proximity sensor.
  * \return bool : Boolean value verifying the end of the calibration sequence.
  */
bool axialMotor::runAxialCalibration()
{
    setMotorState(1);
    //Serial.print("le moteur tourne maintenant");
    while (shouldSlowDown() == false)
    {
       if (shouldSlowDown() == true)
        {
           setMotorState(-1);
           return true; 
        }
    }
  return false;

}

/** \brief Sets the motor state value to a given value of 0,1 or -1. If the value is not in this range, the function forces -1. It then changes the pin output to the motor accordingly
 *  \param StateValue : value confirming if the motor should slow down or not.
 */
void axialMotor::setMotorState(int stateValue)
{
  //Serial.println("JE PASSE ICI");
    //Serial.println(stateValue);

  if (stateValue != -1 && stateValue != 1 && stateValue != 0)
     {
        //Serial.println("MAUVAISE ENTRÉE, MAINTENANT MOTORSTATE SERA DE :");
        
        stateValue = -1; //doesn't move the motor
     }
  //Serial.println("STATE VALUE correct");
  motorState = stateValue; //Sets the motor value to the new direction value.
   
  if (motorState == 1) //Changes the motor rotation by changing output pin value.
     {
       //Serial.println("ICI SI LE STATE VALUE EST DE 1");
       
       digitalWrite(getMotorPin(1),HIGH);
       digitalWrite(getMotorPin(2),LOW);
       //Serial.print(digitalRead(getMotorPin(1)));
       //Serial.print(digitalRead(getMotorPin(2)));
     }
     
  else if (motorState == 0)
     {
      // Serial.println("ICI SI LE STATE VALUE EST DE 0");
       digitalWrite(getMotorPin(2),HIGH);
       digitalWrite(getMotorPin(1),LOW);
     }
       /* for(int motorValue = 0 ; motorValue <= 255; motorValue +=5)  //CECI EST A ADAPTER POUR ANALOG
        {
          analogWrite(motorPin, motorValue); 
          delay(30);    
        } */
     
  else if (motorState == -1)
     {
      // Serial.print("ICI SI LE STATE VALUE EST DE -1");
       digitalWrite(getMotorPin(2),LOW);
       digitalWrite(getMotorPin(1),LOW);
     }
}

/** \brief gets the motor current state. 
 *  \return int : current state value of the motor.
 */
int axialMotor::getMotorState()
{
  return motorState;
}
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

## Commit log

2020-01-22 motor control, ui file opened directly
2020-01-31 Added vertical axis calibration button
2020-02-01 Added in the sequence tab a right click menu on the list and move the delete button there Added a class for motors
2020-02-05 arduino code
2020-02-06 arduino serial communication
2020-02-10 Added a list of the saved moves in a sequence. It is now also possible to double click those moves to print the numbers of the motors for now
2020-02-13 Finalisation of the motor's softlimit code.
2020-02-15 Implementation of the Axial calibration (runAxialCalibration()) as well as a SetAxialMotorDirection() and checkAxialMotorDirection(). THESE FUNCTIONS NEED TO BE TESTED AND COMPLETED (especially runAx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
2020-02-18 Message reception thread
2020-02-21 Update current motor position with incomming messages and initialize slider positions.
2020-02-25 Arduino code documentation
2020-02-25 Refactoring of the axial motor. It is now a class containing the proximity sensors as well as motor attributes.
2020-02-25 Send command to motor
2020-02-25 fix Motor class
2020-02-26 Prototype Assembly CAD
    [535130 assembly.SLDPRT, 585416.SLDPRT, 585424.SLDPRT, 585446.SLDPRT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]
2020-02-26 Prototype BOM
    [BOM_proto.xlsx]
2020-03-11 Outgoing message flow limit
2020-03-13 Update axialMotor.h
    Motor code now works and home well with bool control.
2020-03-24 The sequences and moves are now linked to the actual motors, updated sliders positions in certain context when we moved the robot but the sliders stayed at their old positions. Also changed the speed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
2020-03-31 We now also save the last port used and the play sequence is in a thread
2020-03-31 Added sldparts of arm shell
    [coin_baseV2_top.SLDPRT, coin_baseV2_troue.SLDPRT]
2020-04-08 Added BOM for shell and assembling directions
    [shell_BOM.xlsx]
2020-04-08 Added second shell and assembly
    [coin_baseV2_top.SLDPRT, coin_baseV2_troue.SLDPRT, second.SLDPRT]
2020-04-08 Update of CAD, ASSEMBLY_INSTRUCTIONS and BOM
    [535130 assembly.SLDPRT, 585416.SLDPRT, 585424.SLDPRT, 585446.SLDPRT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]
2020-04-18 Added tests for the handler of the list of sequences and fixed the casting of the motor position in the OpenCr code
2020-04-20 Wiring image problem
    Reupload of the image.
